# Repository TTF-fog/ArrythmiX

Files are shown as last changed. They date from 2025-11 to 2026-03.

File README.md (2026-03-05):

# Main Repo
> For Blueprint Reviewers, [Final Version](Hardware/CAD/the_last_one.step) is what our end CAD model is. Design is goose.f3d present in the same file. BOM is present in root dir, [table format](#BOM) (collapsed) at bottom of readme and [PCB folder](Hardware/PCB). PCB Folder contains gerbers.zip and design files. Firmware is in [firmware](src) and software in [software](scripts). Everything else is in ML or doc. Check [Sections](#sections) for descriptions. thank you for reviewing our project :)

This is the main repo for the Arryhtmix Project, which aims to develop a novel, end-to-end framework for
the prediction of cardiac events

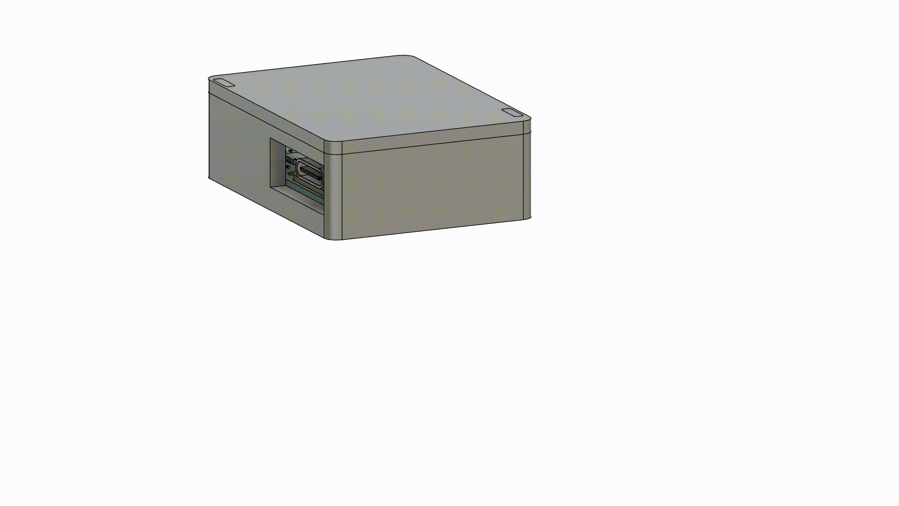
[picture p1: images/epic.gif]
VERY EPIC GIF IF BROKEN PLEASE WATCH

>
> We have developed a novel end to end pipeline for the prediction of cardiac arrests through machine learning alongside a medical device to facilitate the collection of data for the model.
>
>The initial process takes place on the device. The single-lead AD8232 Sensor with integrated hardware high pass and low pass filters collects ECG Data from one lead with one electrode for common mode rejection. The data is read at a rate of 360 Hz by the nRF52840 using a 12-bit ADC and concurrently denoised through an integrated LSM6DS3. While the device is idle, it is kept in deep sleep mode, significantly reducing power consumption.
>Upon the collection of 10 data points, the buffer is dispatched using BLE to the host device.
> 
>Upon being dispatched to the host device, two models are run on it. First, an Arrhythmia classification model based on the MIT-BIH dataset and architected with a BiLSTM and Random Forest classifier returns a dataclass which describes the type of arrhythmia if any. Secondly, a novel hybrid CNN-LSTM model trained on the Sudden Cardiac Arrest Holter Database predicts ventricular fibrillation risk across four temporal categories. The models have been quantised for edge deployment and offer platform flexibility. A f-score of 99 percent and of 85 percent is obtained from both models respectively.
>
- ISEF Abstract
### Sections
- [Scripts](scripts)
  - [Miscellaneous](scripts/misc)
    - mixture of normal and vibecoded scripts made for testing
  - [Rerun](scripts/rerun)
    - Scripts and Blueprints for the [Rerun](https://rerun.io) visualizer
- [Hardware](Hardware)
  - [PCB Documents](Hardware/PCB)
  - [CAD Files](Hardware/CAD)
    - all of these are from some iteration or the other, but they should represent the totality of our cad.
    - [Final Version](Hardware/CAD/the_last_one.step) is what our end model is. Design is goose.f3d present in the same file
- [Firmware](src)
  - firmware for the device
- [ML](ML)
  - Our own model training stuff, and tweaked versions of other's
- [Documentation](Doc) 
  - Extra stuff relating to the project. Will add slide decks soon:tm:
### Images 
<details>

<summary> Machine Learning </summary>

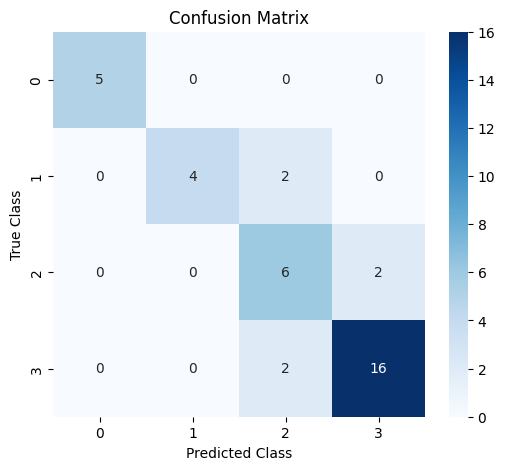
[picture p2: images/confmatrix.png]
confusion matrix


> Confusion Matrix

<br>
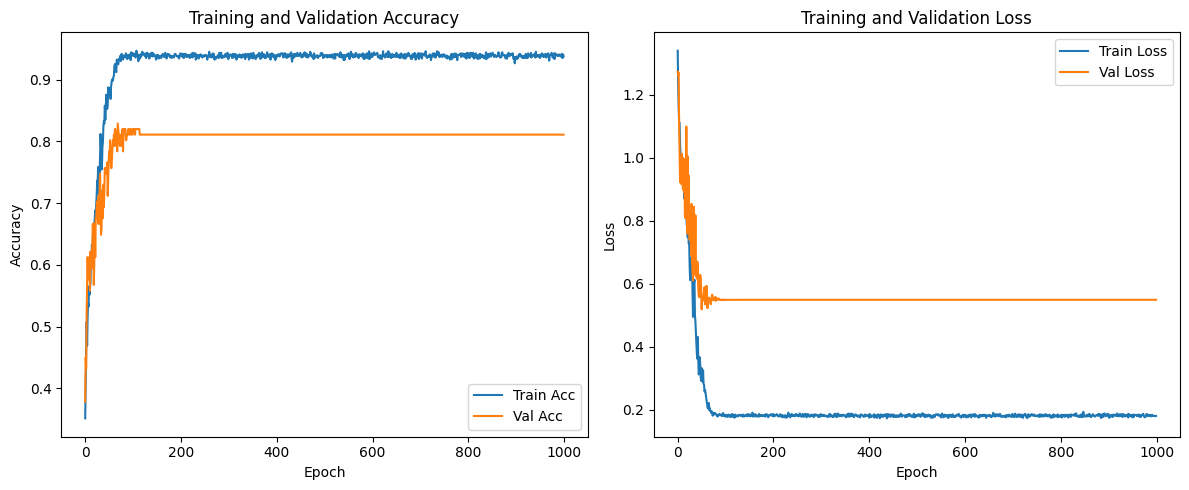
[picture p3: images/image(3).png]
train and vall graphs
  

> train and valuation graphs

<br>

</details>

<details>

<summary>Software</summary>

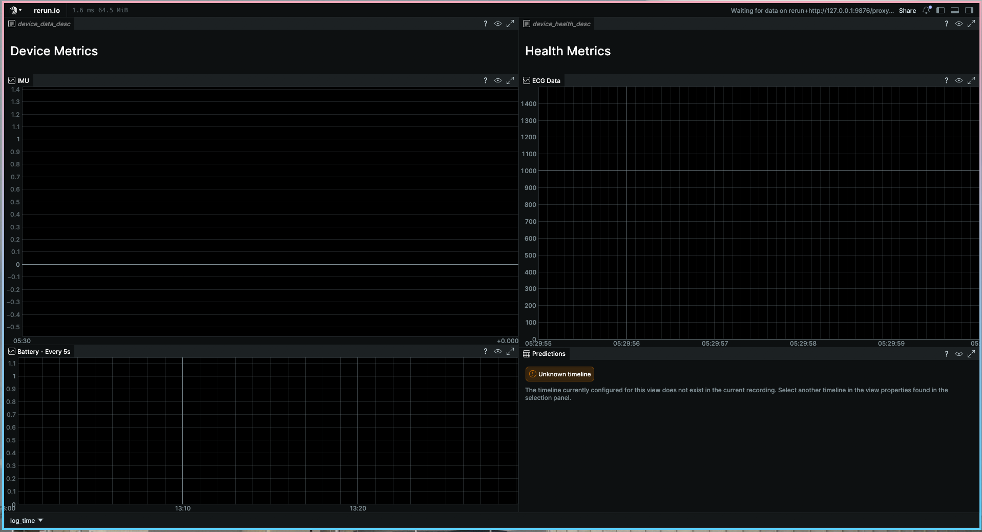
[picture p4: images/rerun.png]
Rerun Dashboard (No Data)


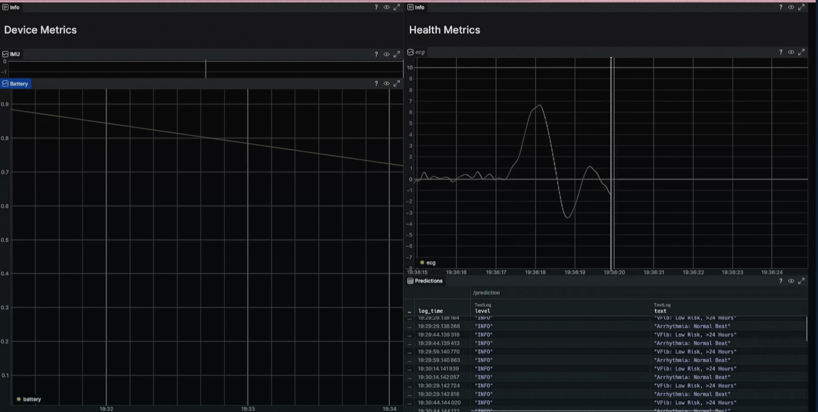
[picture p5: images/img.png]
Machine

<br>

</details>

<details>

<summary>Hardware</summary>

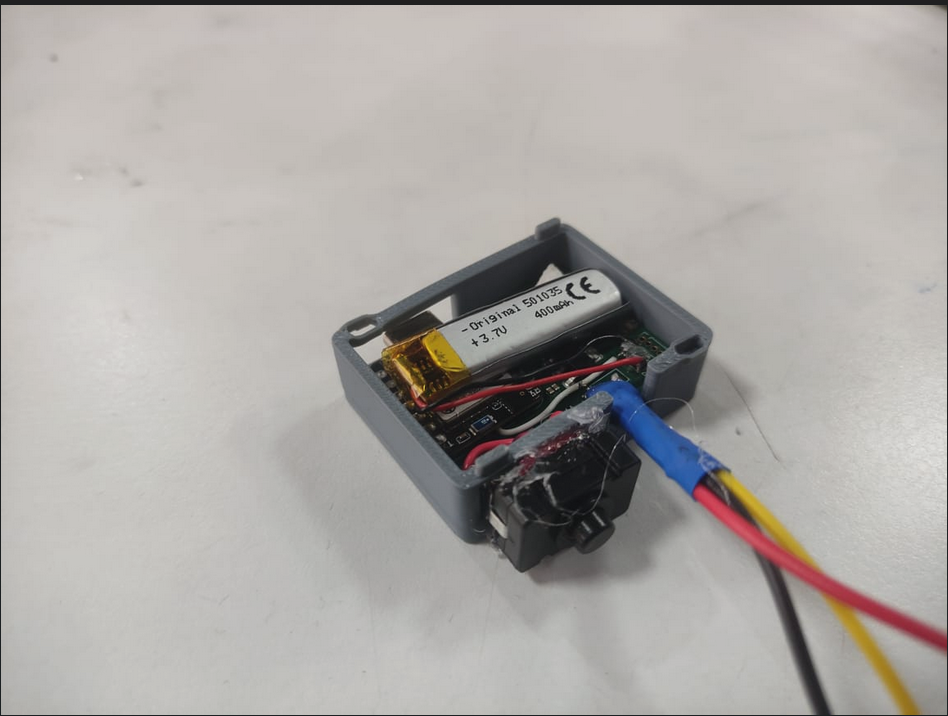
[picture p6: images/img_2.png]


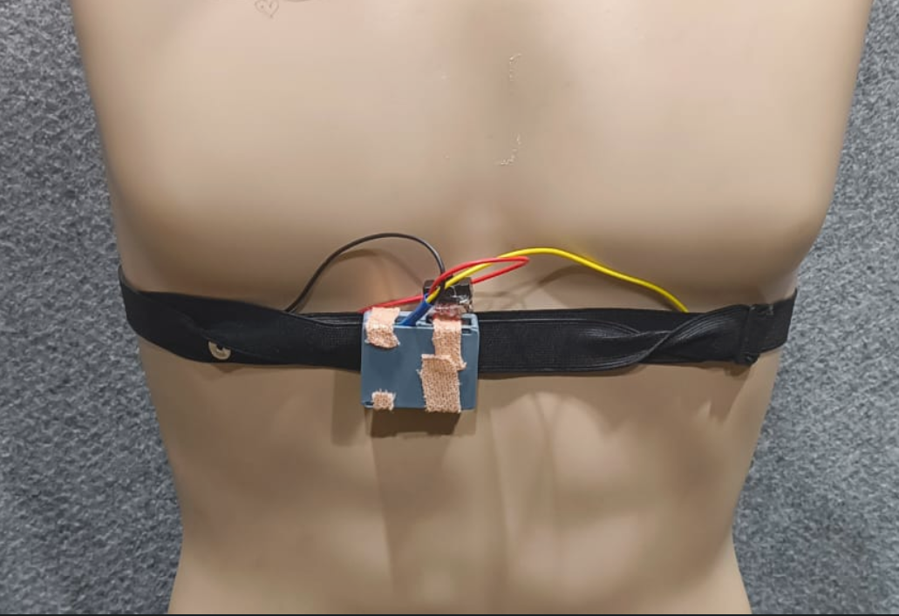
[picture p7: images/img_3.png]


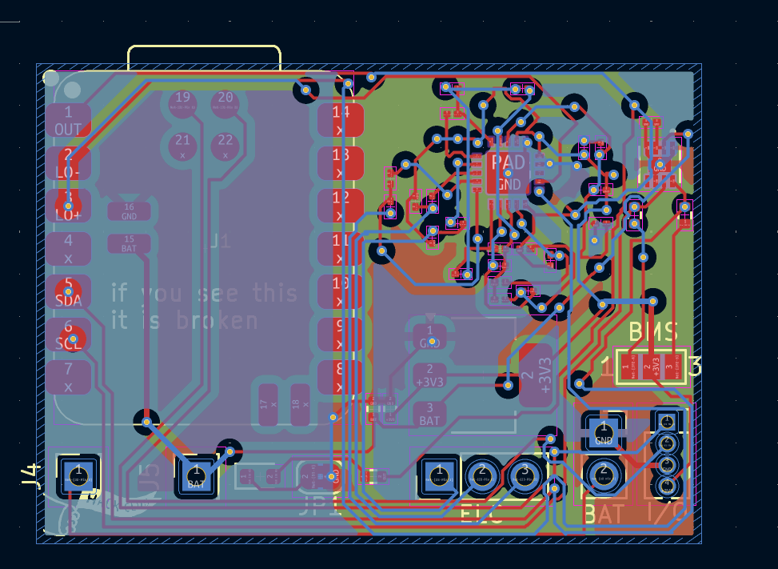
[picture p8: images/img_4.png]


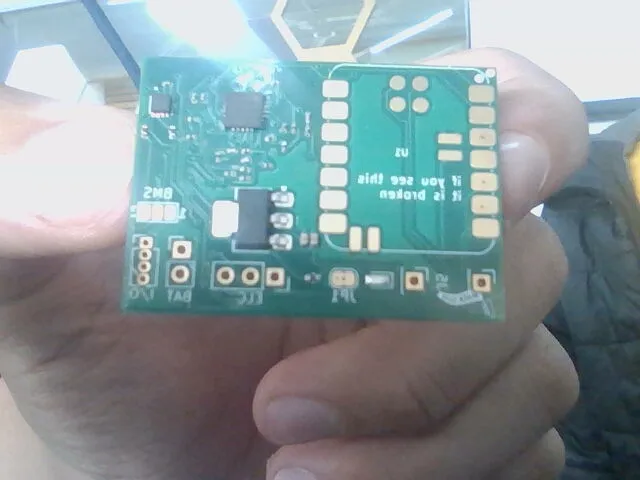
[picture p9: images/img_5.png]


> unsoldered, sorry for bad quality

<br>

</details>

<details>

<summary>CAD Models</summary>

3D Model

> click to see preview
</details>

### Bill Of Materials
<details id="BOM">

<summary> Bill Of Materials for PCB</summary>

| JLCPCB BOM Tool - BOM Matching           |                   |                    |                                                                |               |                    |                    |                                                                                                                                                           |               |                                                                                                                                                                                  |                                                            |                                                                                                                       |                   |                                                                           |          |     |           |                 |
|------------------------------------------|-------------------|--------------------|----------------------------------------------------------------|---------------|--------------------|--------------------|-----------------------------------------------------------------------------------------------------------------------------------------------------------|---------------|----------------------------------------------------------------------------------------------------------------------------------------------------------------------------------|------------------------------------------------------------|-----------------------------------------------------------------------------------------------------------------------|-------------------|---------------------------------------------------------------------------|----------|-----|-----------|-----------------|
| BOM name：bom-JLCPCB Assembly Order.xlsx |                   |                    | Download Time：2025-12-03 19:28:29                             |               |                    |                    | * Our matching results are updated in real-time, but stock and prices may change.  If it's been over 24 hours, please re-match before placing your order. |               |                                                                                                                                                                                  |                                                            |                                                                                                                       |                   |                                                                           |          |     |           |                 |
| PCB Assembled Qty：5                     |                   |                    | Est. Total Price：11.8136                                      |               |                    |                    |                                                                                                                                                           |               |                                                                                                                                                                                  |                                                            |                                                                                                                       |                   |                                                                           |          |     |           |                 |
| Your BOM                                 |                   |                    |                                                                |               | Matched Parts      |                    |                                                                                                                                                           |               |                                                                                                                                                                                  |                                                            |                                                                                                                       | Order Information |                                                                           |          |     |           |                 |
| Top Designator                           | Bottom Designator | Comment            | Footprint                                                      | JLCPCB Part # | Matches            | Part #             | Manufacturer                                                                                                                                              | Footprint     | Description                                                                                                                                                                      | Category                                                   | Warning                                                                                                               | JLCPCB Part #     | Product link                                                              | Lib Type | Qty | Source    | Total Price ($) |
| C2                                       |                   | 1nF                | C_0201_0603Metric                                              |               | Select by Customer | 0201B102K500NT     | FH (Guangdong Fenghua Advanced Tech)                                                                                                                      | 0201          | 1nF 50V X7R ±10% 0201 Multilayer Ceramic Capacitors MLCC - SMD/SMT ROHS                                                                                                          | Multilayer Ceramic Capacitors MLCC - SMD/SMT               |                                                                                                                       | C66942            | https://jlcpcb.com/partdetail/68029-0201B102K500NT/C66942                 | Extended | 20  | 20 JLCPCB | 0.014           |
| C5                                       |                   | 1.5nF              | C_0201_0603Metric                                              |               | Select by Customer | GRM033R71C152KA01D | Murata Electronics                                                                                                                                        | 0201          | 1.5nF 16V X7R ±10% 0201 Multilayer Ceramic Capacitors MLCC - SMD/SMT ROHS                                                                                                        | Multilayer Ceramic Capacitors MLCC - SMD/SMT               |                                                                                                                       | C161482           | https://jlcpcb.com/partdetail/172863-GRM033R71C152KA01D/C161482           | Extended | 20  | 20 JLCPCB | 0.05            |
| C6                                       |                   | 10nF               | C_0201_0603Metric                                              |               | Select by Customer | GRM033R61E103KA12D | Murata Electronics                                                                                                                                        | 0201          | 10nF 25V X5R ±10% 0201 Multilayer Ceramic Capacitors MLCC - SMD/SMT ROHS                                                                                                         | Multilayer Ceramic Capacitors MLCC - SMD/SMT               |                                                                                                                       | C76938            | https://jlcpcb.com/partdetail/MurataElectronics-GRM033R61E103KA12D/C76938 | Extended | 20  | 20 JLCPCB | 0.036           |
| C7,C1                                    |                   | 0.33uF             | C_0201_0603Metric                                              |               | Select by Customer | GRM033R61E334KE15D | Murata Electronics                                                                                                                                        | 0201          | 25V 330nF ±10% 0201 Multilayer Ceramic Capacitors MLCC - SMD/SMT ROHS                                                                                                            | Multilayer Ceramic Capacitors MLCC - SMD/SMT               | 1.The comment (GRM033R61E334KE15D) of this part does not match the one (0.33uF) provided in your BOM. Please confirm; | C723889           | https://jlcpcb.com/partdetail/768943-GRM033R61E334KE15D/C723889           | Extended | 20  | 20 JLCPCB | 0.388           |
| C8,C9                                    |                   | 10uF               | C_0402_1005Metric                                              |               | Select by System   | CL05A106MQ5NUNC    | Samsung Electro-Mechanics                                                                                                                                 | 0402          | 10uF 6.3V X5R ±20% 0402 Multilayer Ceramic Capacitors MLCC - SMD/SMT ROHS                                                                                                        | Multilayer Ceramic Capacitors MLCC - SMD/SMT               |                                                                                                                       | C15525            | https://jlcpcb.com/partdetail/16204-CL05A106MQ5NUNC/C15525                | Basic    | 20  | 20 JLCPCB | 0.09            |
| C10,C4,C3                                |                   | 0.1uF              | C_0201_0603Metric                                              |               | Select by Customer | CL03A104KP3NNNC    | Samsung Electro-Mechanics                                                                                                                                 | 0201          | 100nF 10V X5R ±10% 0201 Multilayer Ceramic Capacitors MLCC - SMD/SMT ROHS                                                                                                        | Multilayer Ceramic Capacitors MLCC - SMD/SMT               | 1.The comment (CL03A104KP3NNNC) of this part does not match the one (0.1uF) provided in your BOM. Please confirm;     | C49062            | https://jlcpcb.com/partdetail/50070-CL03A104KP3NNNC/C49062                | Extended | 20  | 20 JLCPCB | 0.026           |
| D1                                       |                   | LED                | LED_0603_1608Metric                                            |               | Unconfirmed        | KT-0603R           | Hubei KENTO Elec                                                                                                                                          | 0603          | -40℃~+85℃ 120° 2.4V 20mA 300mcd 40mW 615nm~630nm 645nm Red Water Clear 0603 LED Indication - Discrete ROHS                                                                       | LED Indication - Discrete                                  | 1.The comment (KT-0603R) of this part does not match the one (LED) provided in your BOM. Please confirm;              | C2286             | https://jlcpcb.com/partdetail/Hubei_KENTOElec-KT0603R/C2286               | Basic    | 20  | 20 JLCPCB | 0.112           |
| R1,R4,R7,R5,R6,R15                       |                   | 10M惟              | R_0201_0603Metric                                              |               | Select by Customer | RTT01106JTH        | RALEC                                                                                                                                                     | 0201          | -55℃~+125℃ 10MΩ 25V 50mW Thick Film Resistor ±200ppm/℃ ±5% 0201 Chip Resistor - Surface Mount ROHS                                                                               | Chip Resistor - Surface Mount                              | 1.The comment (RTT01106JTH) of this part does not match the one (10M惟) provided in your BOM. Please confirm;         | C158867           | https://jlcpcb.com/partdetail/RALEC-RTT01106JTH/C158867                   | Extended | 22  | 22 JLCPCB | 0.0198          |
| R3,R2                                    |                   | 180k惟             | R_0201_0603Metric                                              |               | Select by Customer | RTT01184JTH        | RALEC                                                                                                                                                     | 0201          | -55℃~+125℃ 180kΩ 25V 50mW Thick Film Resistor ±200ppm/℃ ±5% 0201 Chip Resistor - Surface Mount ROHS                                                                              | Chip Resistor - Surface Mount                              | 1.The comment (RTT01184JTH) of this part does not match the one (180k惟) provided in your BOM. Please confirm;        | C158738           | https://jlcpcb.com/partdetail/RALEC-RTT01184JTH/C158738                   | Extended | 20  | 20 JLCPCB | 0.068           |
| R8                                       |                   | 360k               | R_0201_0603Metric                                              |               | Select by Customer | RTT01364JTH        | RALEC                                                                                                                                                     | 0201          | -55℃~+125℃ 25V 360kΩ 50mW Thick Film Resistor ±200ppm/℃ ±5% 0201 Chip Resistor - Surface Mount ROHS                                                                              | Chip Resistor - Surface Mount                              | 1.The comment (RTT01364JTH) of this part does not match the one (360k) provided in your BOM. Please confirm;          | C158574           | https://jlcpcb.com/partdetail/RALEC-RTT01364JTH/C158574                   | Extended | 20  | 20 JLCPCB | 0.022           |
| R9,R13,R14                               |                   | 1M惟               | R_0201_0603Metric                                              |               | Select by Customer | RTT011004FTH       | RALEC                                                                                                                                                     | 0201          | -55℃~+125℃ 1MΩ 25V 50mW Thick Film Resistor ±1% ±200ppm/℃ 0201 Chip Resistor - Surface Mount ROHS                                                                                | Chip Resistor - Surface Mount                              | 1.The comment (RTT011004FTH) of this part does not match the one (1M惟) provided in your BOM. Please confirm;         | C102686           | https://jlcpcb.com/partdetail/RALEC-RTT011004FTH/C102686                  | Extended | 20  | 20 JLCPCB | 0.018           |
| R12                                      |                   | 100k惟             | R_0201_0603Metric                                              |               | Select by Customer | CR0201FH1003G      | LIZ Elec                                                                                                                                                  | 0201          | -55℃~+125℃ 100kΩ 25V 50mW Thick Film Resistor ±1% ±250ppm/℃ 0201 Chip Resistor - Surface Mount ROHS                                                                              | Chip Resistor - Surface Mount                              | 1.The comment (CR0201FH1003G) of this part does not match the one (100k惟) provided in your BOM. Please confirm;      | C100127           | https://jlcpcb.com/partdetail/LIZElec-CR0201FH1003G/C100127               | Extended | 20  | 20 JLCPCB | 0.016           |
| R16                                      |                   | 1.4m惟             | R_0201_0603Metric                                              |               | Select by Customer | 0201WMF1404TEE     | UNI-ROYAL(Uniroyal Elec)                                                                                                                                  | 0201          | -55℃~+155℃ 1.4MΩ 25V 50mW Thick Film Resistor ±1% ±200ppm/℃ 0201 Chip Resistor - Surface Mount ROHS                                                                              | Chip Resistor - Surface Mount                              |                                                                                                                       | C423737           | https://jlcpcb.com/partdetail/416687-0201WMF1404TEE/C423737               | Extended | 20  | 20 JLCPCB | 0.028           |
| R19                                      |                   | 1k                 | R_0402_1005Metric                                              |               | Select by Customer | 0402WGF1001TCE     | UNI-ROYAL(Uniroyal Elec)                                                                                                                                  | 0402          | -55℃~+155℃ 1kΩ 50V 62.5mW Thick Film Resistor ±1% ±100ppm/℃ 0402 Chip Resistor - Surface Mount ROHS                                                                              | Chip Resistor - Surface Mount                              | 1.The comment (0402WGF1001TCE) of this part does not match the one (1k) provided in your BOM. Please confirm;         | C11702            | https://jlcpcb.com/partdetail/12256-0402WGF1001TCE/C11702                 | Basic    | 20  | 20 JLCPCB | 0.012           |
| R21,R20                                  |                   | 2.2K               | R_0402_1005Metric                                              |               | Select by Customer | 0402WGF2201TCE     | UNI-ROYAL(Uniroyal Elec)                                                                                                                                  | 0402          | -55℃~+155℃ 2.2kΩ 50V 62.5mW Thick Film Resistor ±1% ±100ppm/℃ 0402 Chip Resistor - Surface Mount ROHS                                                                            | Chip Resistor - Surface Mount                              | 1.The comment (0402WGF2201TCE) of this part does not match the one (2.2K) provided in your BOM. Please confirm;       | C25879            | https://jlcpcb.com/partdetail/26622-0402WGF2201TCE/C25879                 | Basic    | 20  | 20 JLCPCB | 0.012           |
| U2                                       |                   | AD8232             | LFCSP_20                                                       |               | Unconfirmed        | AD8232ACPZ-R7      | Analog Devices                                                                                                                                            | LFCSP-20(4x4) | -40℃~+85℃ 12ppm/℃ 170uA 2V~3.5V LFCSP-20(4x4) Analog Front End (AFE) ROHS                                                                                                        | Analog To Digital Converters (ADC)                         | 1.The comment (AD8232ACPZ-R7) of this part does not match the one (AD8232) provided in your BOM. Please confirm;      | C43216            | https://jlcpcb.com/partdetail/AnalogDevices-AD8232ACPZR7/C43216           | Extended | 2   | 2 JLCPCB  | 5.715           |
| U3                                       |                   | NCP1117-3.3_SOT223 | SOT-223-3_TabPin2                                              |               | Select by Customer | AMS1117-3.3        | Advanced Monolithic Systems                                                                                                                               | SOT-223       | -40℃~+125℃ 0.003%Vout 1 1.1V@(800mA) 16V 1A 3.3V 5mA 72dB@(120Hz) Fixed Over Current Protection Positive SOT-223 Voltage Regulators - Linear, Low Drop Out (LDO) Regulators ROHS | Voltage Regulators - Linear, Low Drop Out (LDO) Regulators |                                                                                                                       | C6186             | https://jlcpcb.com/partdetail/Advanced_MonolithicSystems-AMS1117_33/C6186 | Basic    | 2   | 2 JLCPCB  | 0.3178          |
| U4                                       |                   | MAX17048G_T10      | SON50P200X200X80-9N                                            |               | Select by System   | MAX17048G+T10      | Analog Devices Inc./Maxim Integrated                                                                                                                      | DFN-8-EP(2x2) | -40℃~+85℃ 1 2.5V~4.5V 3uA I2C Lithium Battery Not Supported Not Supported DFN-8-EP(2x2) Battery Management ROHS                                                                  | Battery Management                                         |                                                                                                                       | C2682616          | https://jlcpcb.com/partdetail/2777647-MAX17048GT10/C2682616               | Extended | 2   | 2 JLCPCB  | 4.869           |
| J1                                       |                   | DNP                | PinSocket_1x04_P1.27mm_Vertical                                |               | No matches         | No Part Selected   |                                                                                                                                                           |               |                                                                                                                                                                                  |                                                            |                                                                                                                       |                   |                                                                           |          |     |           |                 |
| J2                                       |                   | DNP                | PinSocket_1x02_P2.54mm_Vertical                                |               | No matches         | No Part Selected   |                                                                                                                                                           |               |                                                                                                                                                                                  |                                                            |                                                                                                                       |                   |                                                                           |          |     |           |                 |
| J3                                       |                   | DNP                | PinHeader_1x03_P2.54mm_Vertical                                |               | No matches         | No Part Selected   |                                                                                                                                                           |               |                                                                                                                                                                                  |                                                            |                                                                                                                       |                   |                                                                           |          |     |           |                 |
| SW1                                      |                   | SW_SPST            | SW_DIP_SPSTx01_Slide_6.7x4.1mm_W6.73mm_P2.54mm_LowProfile_JPin |               | No matches         | No Part Selected   |                                                                                                                                                           |               |                                                                                                                                                                                  |                                                            |                                                                                                                       |                   |                                                                           |          |     |           |                 |
| U1                                       |                   | XIAO-nRF52840-SMD  | XIAO-nRF52840-SMD                                              |               | No matches         | No Part Selected   |                                                                                                                                                           |               |                                                                                                                                                                                  |                                                            |                                                                                                                       |                   |                                                                           |          |     |           |                 |

</details>

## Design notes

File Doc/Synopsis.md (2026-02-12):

A novel pipeline for the prediction of cardiac events through machine learning, integrated with a loww cost, long term and reusable Holter monitor.

Introduction
Cardiovascular disease is a major health concern globally, with it accounting for nearly 1/4th of all deaths per year in India (Volkov, 2015). The very abrupt nature of Sudden Cardiac Death(SCD) and other cardiac events leads to a slow response time, greatly increasing mortality. This represents three pressing concerns in healthcare:
(A) a lack of reusable Holter monitors made for long term monitoring,
(B) an absence of short-term (under one day) prediction of cardiac events like Sudden Cardiac Death and Myocardial Infarctions,
(C) a lack of integration of machine learning and other computer-assisted analytical methods with wearable ECG devices like Holter Monitors and fitness activity monitors.
The primary objective of our work is to solve these problems by creating an accurate, power-efficient method to predict cardiac events in the short term, integrated with a low-cost wearable Holter patch under $30 (~2600 INR).

Innovation
Our work introduces a low-cost, power-efficient system architecture for short-term cardiac event prediction through an integrated wearable and machine learning pipeline. Unlike conventional Holter monitors that depend on retrospective data analysis, the proposed design incorporates real-time preprocessing, motion-compensated noise suppression, wireless transmission and real-time analysis. Our novel machine learning framework comprises two stages: a BiLSTM-based arrhythmia classifier trained on the MIT-BIH Arrhythmia Database (F1-score: 99%) and a hybrid CNN-LSTM predictive model (F1-score: 92%) trained on the Sudden Cardiac Arrest Holter Database to anticipate ventricular fibrillation (VFib, a critical precursor to cardiac arrest) onset. To our knowledge, an ML-integrated low-cost reusable Holter monitor is not present in the current literature or deployment. Additionally, a short-term (> 24-hour timeframe) predictive model for cardiac events is also absent from the current literature.

Algorithmic Design
Several algorithmic components were integrated to ensure maximum predictive performance. Initial processing takes place on the device itself. The AD8232, which records the ECG, contains an onboard high pass, low pass and RFI filter. Additionally, motion artefact reduction is achieved using an adaptive filtering algorithm, specifically Recursive Least Squares (RLS) or Normalised Least Mean Squares (NLMS), with the LM6 accelerometer signal serving as the noise reference. The subsequent machine learning pipeline is split into two stages, with the first stage being a BiLSTM(Bi-Directional Long Short Term Memory) classifier trained on the MIT-BIH Arrhythmia Database to identify and label certain medically significant arrhythmias and beats, achieving an F1-score of 99% The second stage utilises a hybrid CNN-LSTM model trained on the Sudden Cardiac Arrest Holter Database to estimate ventricular fibrillation (VFib) onset, achieving an F1-score of 92% This model assigns ECG segments to four temporal risk categories—low (>24 hours), medium (<12 hours), high (6–12 hours), and critical (<6 hours). This pipeline is optimized for edge deployment, permitting host device flexibility.

Methodology
To ensure user comfort during prolonged use, a breathable, single-lead patch composed of soft, flexible bandaging material with three embedded electrodes was developed, addressing the discomfort and limitations associated with traditional foam electrodes unsuitable for extended monitoring. ECG acquisition is conducted via the AD8232 analog front-end, which integrates a two-pole high-pass, three-pole low-pass, and on-chip radio frequency interference filter to mitigate baseline drift, high-frequency noise, and electromagnetic interference. Real-time motion artefact mitigation employs adaptive filtering algorithms, either Recursive Least Squares (RLS) or Normalised Least Mean Squares (NLMS), using the LSM6DS3 accelerometer signal as a reference input for dynamic noise cancellation. The nRF52840 SoC utilises a 12-bit ADC sampling at 360 Hz and low-latency, energy-efficient Bluetooth Low Energy transmission to the host device. Before machine learning, the data was resampled to 250 Hz to maintain parity with our machine learning model. On the host, a two-stage machine learning pipeline executes inference: Initially, a BiLSTM classifier trained on the MIT-BIH Arrhythmia Database achieves a 99 % F1-score in arrhythmia detection; subsequently, a hybrid CNN-LSTM model trained on the Sudden Cardiac Arrest Holter Database (Greenwald, 1986) predicts wwventricular fibrillation risk across four temporal categories with a 92% F1-score. The models have been quantised for edge deployment and offer platform flexibility. Outputs and risk notifications are delivered to users via a dedicated mobile application, with inference currently performed on smartphones.
Outcomes and Conclusion
Our device and machine learning pipeline have demonstrated both theoretical and practical usability. Our device remains compact, easy to wear and long-lasting, with the onboard battery staying on for 3+ days at a time, at a current draw of approximately 15 mA. Our machine learning pipeline presents an F1-score of 99% and 92% in both stages, respectively. This pipeline has been tested live with our device and a laptop as the host device, and is demonstrating excellent accuracy. Please refer to our project video for a more in-depth demonstration of the same. Due to the inherent difficulties of testing in a real-world environment, it has been tested on the CU Ventricular Tachyarrhythmia dataset (F. M et. al, 1986). and shows a disregardable low false positive rate alongside a 94% accuracy. In the immediate future, our goals are to acquire more compute resources to be able to work with the extensive MIMIC (Medical Information Mart for Intensive Care) IV and III datasets. Additionally, we are awaiting the delivery of a compact PCB (Printed Circuit Board) to reduce the footprint of our device and reduce battery usage. Schematics and photos of the same are available in our Project Video.

References
Goldberger, A. L., Amaral, L. A. N., Glass, L., Hausdorff, J. M., Ivanov, P. C., Mark, R. G., Mietus, J. E., Moody, G. B., Peng, C.-K., & Stanley, H. E. (2000). PhysioBank, PhysioToolkit, and PhysioNet: Components of a new research resource for complex physiologic signals. Circulation, 101(23), e215–e220. https://doi.org/10.1161/01.CIR.101.23.e215
Greenwald, S. D. (1986). Development and analysis of a ventricular fibrillation detector (Master’s thesis). Massachusetts Institute of Technology.
Nolle, F. M., Badura, F. K., Catlett, J. M., Bowser, R. W., & Sketch, M. H. (1986). CREI-GARD, a new concept in computerized arrhythmia monitoring systems. Computers in Cardiology, 13, 515–518.
Patel, H. (2023). Outcomes of out of hospital sudden cardiac arrest in India: A review and proposed reforms. Indian Heart Journal, 75(5), 321–326. https://doi.org/10.1016/j.ihj.2023.08.005
Volkov, S. (2015). Cardiovascular diseases India. World Health Organization. https://www.who.int/india/health-topics/cardiovascular-diseases

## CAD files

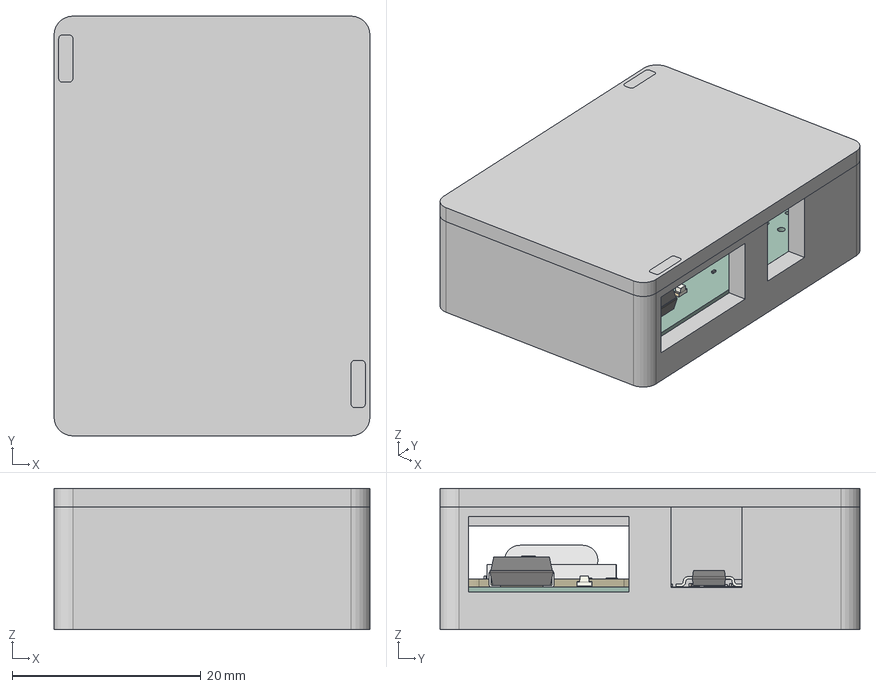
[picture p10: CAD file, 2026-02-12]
Hardware/CAD/main_stp.step
33.5 x 44.5 x 15.0 mm
R_0201_0603Metric x 19
mojo_jojo 1.3.1
C_0402_1005Metric x 2
C_0201_0603Metric x 8
SW_DIP_SPSTx01_Slide_6.7x4.1mm_W6.73mm_P2.54mm_LowProfile_JPin
LED_0603_1608Metric
SOT-223
EMF Shield
Pins 0-6
Pins 7-13
BAT pads
Unpopulated 6 pin pad
JTAG like thing probably
NFC pads
Board:1
R0201:R1
R0201:R2
R0201:R22
R0201:R31
R0201:R32
R0201:R9
R0201:R3
R0201:R4
R0201:R5
R0201:R6
R0201:R7
R0201:R8
R0201:R10
F0603:F1
C0201:C23
C0201:C39
C0201:C40
C0201:C41
C0201:C42
C0201:C43
C0201:C44
C0201:C45
C0201:C48
C0201:C50
C0201:C53
C0201:C54
C0201:C4
C0201:C1
C0201:C2
C0201:C3
C0201:C5
C0201:C6
C0201:C7
C0201:C8
C0201:C9
C0201:C10
C0201:C11
C0201:C12
C0201:C13
C0201:C14
C0201:C49
C0201:C15
R0201:R21
LED-0402:CHG
QFN32G-0.5-5X5MM:U4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

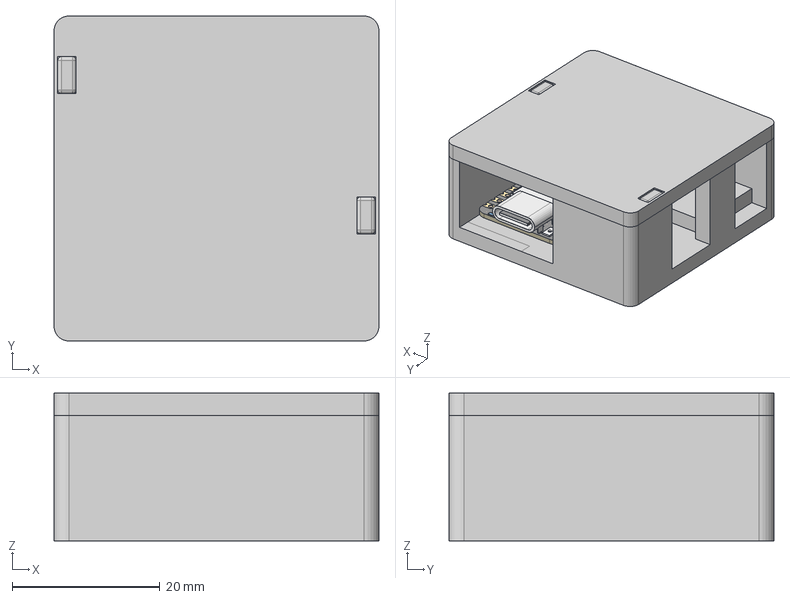
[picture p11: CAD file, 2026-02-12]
Hardware/CAD/the_last_one.step
44.0 x 44.0 x 20.0 mm

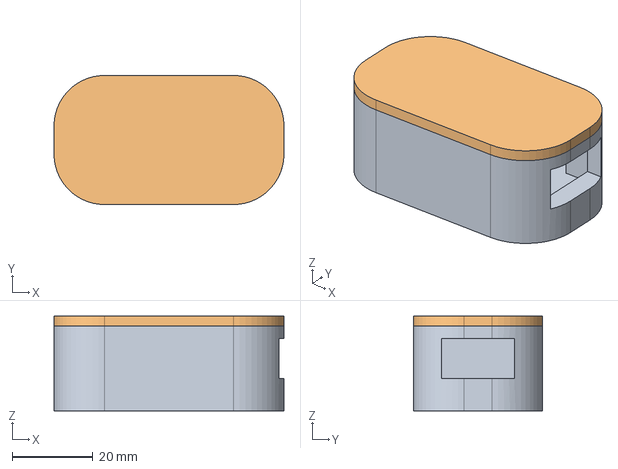
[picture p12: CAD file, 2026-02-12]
Hardware/CAD/capsule_ver_step.step
57.0 x 32.0 x 23.5 mm

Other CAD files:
Hardware/CAD/Design1.f3d
Hardware/CAD/goose.f3d
Hardware/CAD/mainver_f3d.f3z
Hardware/CAD/the_last_one.stl

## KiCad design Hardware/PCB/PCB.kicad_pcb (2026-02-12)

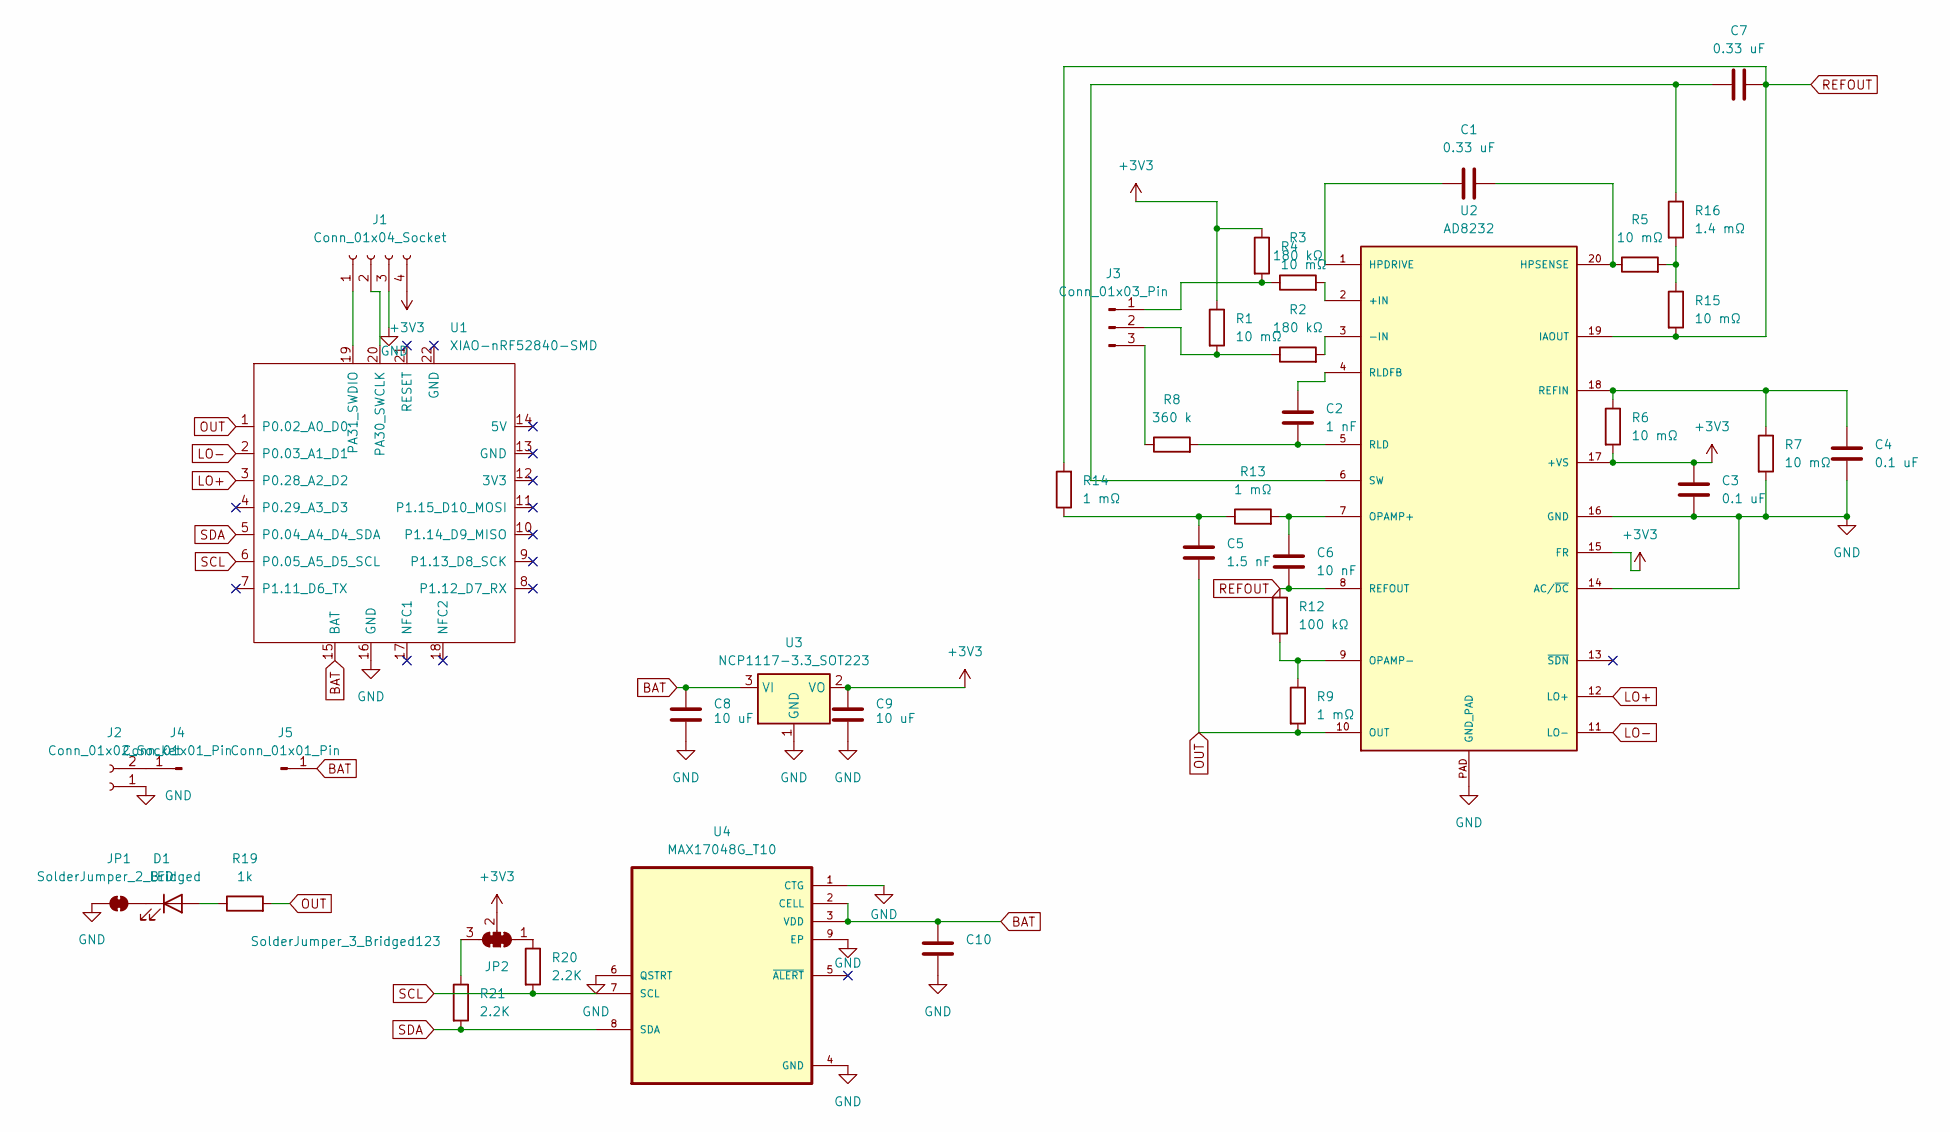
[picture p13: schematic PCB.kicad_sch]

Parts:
C1, C7: 0.33 uF; C_0201_0603Metric
C2: 1 nF; C_0201_0603Metric
C3, C4, C10: 0.1 uF; C_0201_0603Metric
C5: 1.5 nF; C_0201_0603Metric
C6: 10 nF; C_0201_0603Metric
C8, C9: 10 uF; C_0402_1005Metric
D1: LED; LED_0603_1608Metric
J1: Conn_01x04_Socket; PinSocket_1x04_P1.27mm_Vertical
J2: Conn_01x02_Socket; PinSocket_1x02_P2.54mm_Vertical
J3: Conn_01x03_Pin; PinHeader_1x03_P2.54mm_Vertical
J4, J5: Conn_01x01_Pin; PinSocket_1x01_P2.54mm_Vertical
JP1: SolderJumper_2_Bridged; SolderJumper-2_P1.3mm_Bridged2Bar_RoundedPad1.0x1.5mm
JP2: SolderJumper_3_Bridged123; SolderJumper-3_P1.3mm_Open_Pad1.0x1.5mm_NumberLabels
R1, R4, R5, R6, R7, R15: 10 mΩ; R_0201_0603Metric
R2, R3: 180 kΩ; R_0201_0603Metric
R8: 360 k; R_0201_0603Metric
R9, R13, R14: 1 mΩ; R_0201_0603Metric
R12: 100 kΩ; R_0201_0603Metric
R16: 1.4 mΩ; R_0201_0603Metric
R19: 1k; R_0402_1005Metric
R20, R21: 2.2K; R_0402_1005Metric
U1: XIAO-nRF52840-SMD
U2: AD8232; LFCSP_20
U3: NCP1117-3.3_SOT223; SOT-223-3_TabPin2
U4: MAX17048G_T10; SON50P200X200X80-9N

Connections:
+3V3: C3.2, C9.1, J1.4, JP2.2 (C), R1.1, R4.1, R6.2, U2.15 (FR), U2.17 (+VS), U3.2 (VO)
BAT: C8.1, C10.2, J5.1, U1.15 (BAT), U3.3 (VI), U4.2 (CELL), U4.3 (VDD)
GND: C3.1, C4.1, C8.2, C9.2, C10.1, J1.3, J2.1, JP1.1 (A), R7.2, U1.16 (GND), U2.14 (AC/~DC), U2.16 (GND), U2.PAD (GND_PAD), U3.1 (GND), U4.1 (CTG), U4.4 (GND), U4.6 (QSTRT), U4.9 (EP)
LO+: U1.3 (P0.28_A2_D2), U2.12 (LO+)
LO-: U1.2 (P0.03_A1_D1), U2.11 (LO-)
unnamed: C5.2, R13.1, R14.1
unnamed: D1.2 (A), R19.1
unnamed: D1.1 (K), JP1.2 (B)
unnamed: J1.1, U1.19 (PA31_SWDIO)
unnamed: J1.2, U1.20 (PA30_SWCLK)
unnamed: J2.2, J4.1
unnamed: J3.1, R3.1, R4.2
unnamed: J3.2, R1.2, R2.1
unnamed: J3.3, R8.1
unnamed: JP2.1 (A), R20.1
unnamed: JP2.3 (B), R21.1
unnamed: R5.2, R15.1, R16.2
unnamed: R3.2, U2.2 (+IN)
unnamed: R2.2, U2.3 (-IN)
unnamed: C1.1, U2.1 (HPDRIVE)
unnamed: C1.2, R5.1, U2.20 (HPSENSE)
unnamed: C6.2, R13.2, U2.7 (OPAMP+)
unnamed: R9.1, R12.2, U2.9 (OPAMP-)
unnamed: C4.2, R6.1, R7.1, U2.18 (REFIN)
unnamed: C2.2, R8.2, U2.5 (RLD)
unnamed: C2.1, U2.4 (RLDFB)
unnamed: C7.1, R16.1, U2.6 (SW)
OUT: C5.1, R9.2, R19.2, U1.1 (P0.02_A0_D0), U2.10 (OUT)
REFOUT: C6.1, C7.2, R12.1, R14.2, R15.2, U2.8 (REFOUT), U2.19 (IAOUT)
SCL: R20.2, U1.6 (P0.05_A5_D5_SCL), U4.7 (SCL)
SDA: R21.2, U1.5 (P0.04_A4_D4_SDA), U4.8 (SDA)

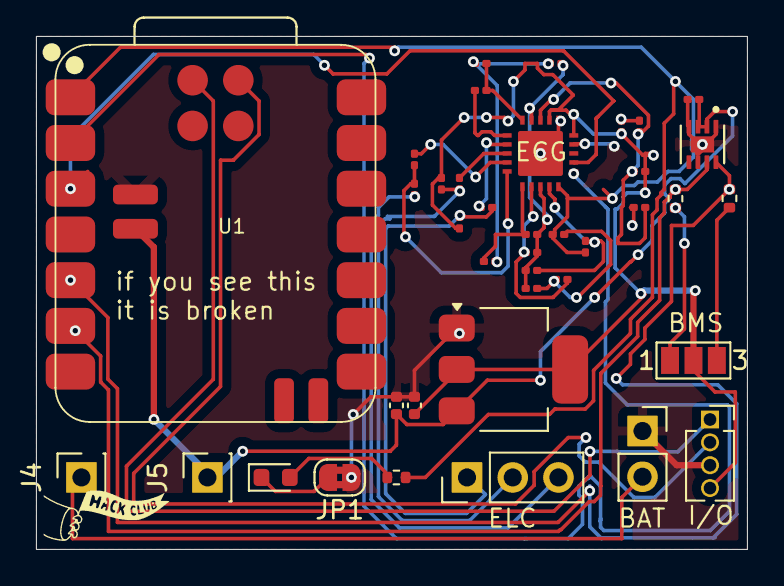
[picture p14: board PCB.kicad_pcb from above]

Board: 4 copper layers, 39.5 x 28.5 mm, 39 parts (0 on the bottom side), 31 nets.

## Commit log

2025-11-07 sleep instead of busy waiting for better power consumption, need to transmit IMU
2026-02-12 gian refactor
    [Design1.f3d, PCB.kicad_pcb, PCB.kicad_sch, bom-JLCPCB Assembly Order(2).xls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]
2026-02-12 fixes and reformats
    [BOM.csv]
2026-03-04 stop bloating up main with stupid commits
    * updates to make it cleaner
    * Update README.md
    * Enhance navigation instructions in README
    Updated README to improve navigation instructions.
    * Fix formatting and update ISEF Abstract section
    ---------
    [the_last_one.stl]
